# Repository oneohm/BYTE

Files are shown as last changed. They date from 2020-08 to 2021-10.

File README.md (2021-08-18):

# The BYTE
Full design package for the BYTE hands free interface

Details are available on the Hackaday project page:`
https://hackaday.io/project/171778-the-byte

## Repository Architecture

This repository is divided by 4 main folders:

- Docs: You'll find here our consult documents, and documentation of the project.
- Firmware: You'll find here everything you need to build the firmware and in case of needed, modify it.
- Hardware: You'll find here the KiCad projects with theirs libraries so the design is fully portable.
- Mechanical: You''ll find here all the FreeCad files to print/modify/understand the mechanics of the device.

You will find more information on each README in each folder, in order to keep this readme short.

# Previous Versions

It's important to note that this repository is under development, if your interested on one "The Byte" device already working, you should jump to the [Realese section](https://github.com/oneohm/BYTE/releases) of this repository to get the V1.0

## Version 1.0 

The version 1.0 has this architecture based on Seeeduino XIAO and all the connection is done by USB.

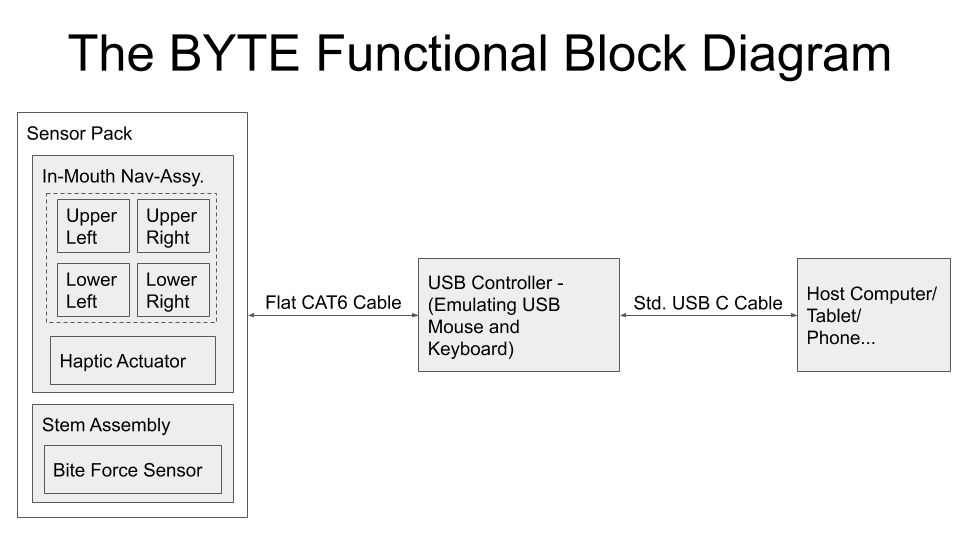
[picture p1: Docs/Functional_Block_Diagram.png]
Architecture


## License Info:

Firmware is licensed under the GNU General Public License v3.0

Hardware design is licensed under <br />This work is licensed under a <a rel="license" href="http://creativecommons.org/licenses/by-nc-sa/4.0/">Creative Commons Attribution-NonCommercial-ShareAlike 4.0 International License</a>.

Once the design is finalized the hardware will recieve a more permissive license.

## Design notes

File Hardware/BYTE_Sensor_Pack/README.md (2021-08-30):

# The BYTE
Full design package for the BYTE hands free interface

Details are available on the Hackaday project page:`
https://hackaday.io/project/171778-the-byte

# Sensor Pack 

 You'll find here the KiCad projects for the different sensor packs.

- BYTE_Sensors.pretty: Library folder for all the KiCad footprints used in the sensor pack development.

- BYTE_FSR: First sensor pack used, only FSR for X/Y axis.
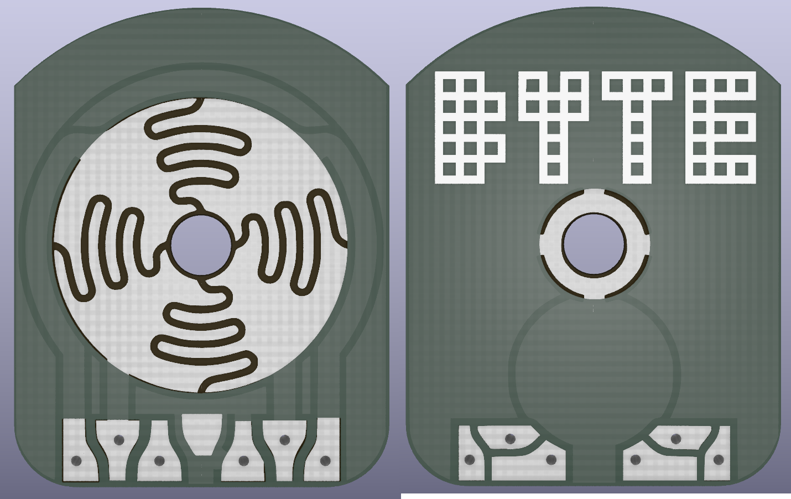
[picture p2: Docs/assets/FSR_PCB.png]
BYTE_FSR

- BYTE_Bite: First sensor pack used, only FSR also for the bite.
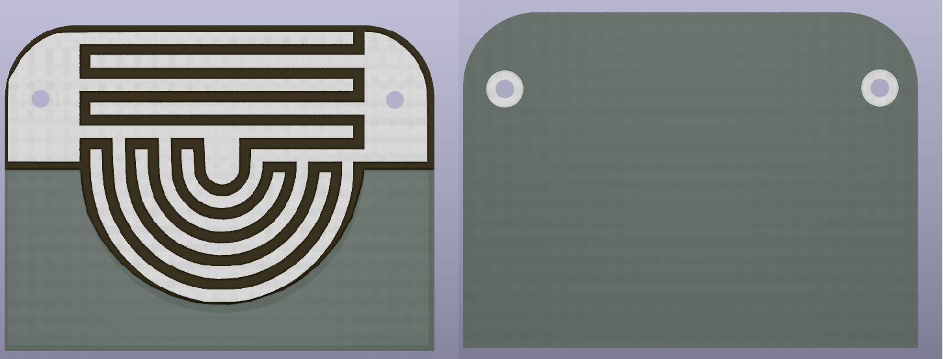
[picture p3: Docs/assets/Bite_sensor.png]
BYTE_Bite

- BYTE_Capacitive: Sensor intended to be used as capacitive feedback for FSR shift error.
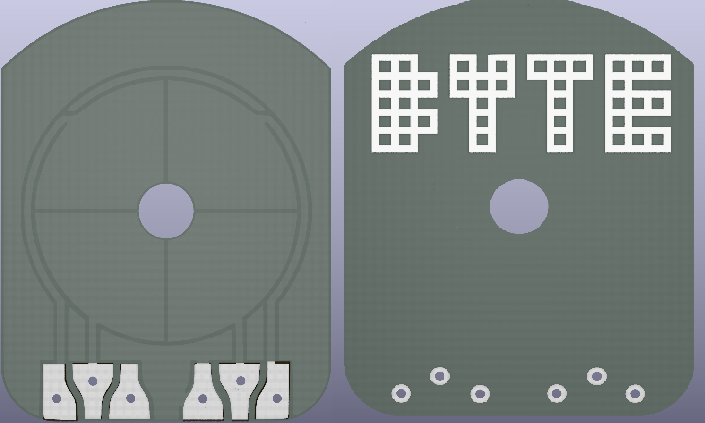
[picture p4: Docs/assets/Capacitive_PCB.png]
BYTE_Capacitive

- ...more to come.

## License Info:

Firmware is licensed under the GNU General Public License v3.0

Hardware design is licensed under <br />This work is licensed under a <a rel="license" href="http://creativecommons.org/licenses/by-nc-sa/4.0/">Creative Commons Attribution-NonCommercial-ShareAlike 4.0 International License</a>.

Once the design is finalized the hardware will recieve a more permissive license.

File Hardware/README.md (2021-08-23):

# The BYTE
Full design package for the BYTE hands free interface

Details are available on the Hackaday project page:`
https://hackaday.io/project/171778-the-byte

# Hardware 

 You'll find here the KiCad projects with theirs libraries so the design is fully portable among other folders with more hardware related information.

- BYTE_Bill_Of_Materials: Bill of materials of the electronics
- BYTE_Controller_PCB:  KiCad project for the main controller.
- BYTE_Full_Schematics: Full schematic in PDF for easy reading without KiCad.
- BYTE_Sensor_Artwork: All SVG files used to convert shapes from FreeCad to KiCad
- BYTE_Sensors_PCB: KiCad projects for the different sensor packs. 

You will find more information on each README in each folder, in order to keep this readme short.

## License Info:

Firmware is licensed under the GNU General Public License v3.0

Hardware design is licensed under <br />This work is licensed under a <a rel="license" href="http://creativecommons.org/licenses/by-nc-sa/4.0/">Creative Commons Attribution-NonCommercial-ShareAlike 4.0 International License</a>.

Once the design is finalized the hardware will recieve a more permissive license.

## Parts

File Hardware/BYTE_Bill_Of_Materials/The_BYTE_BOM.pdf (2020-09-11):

The BYTE BOM [For Prototypes - Production will differ]

Costs are approximate for custom parts

Quantity | Description | Part Type | Manufacturer Part# Unit | Qty per unit | Unit Cost | Extended Cost Product Page/Source/Design...
1 Stem Top - 3D printed, PETG, 100% infill | 3D Printed | N/A | EA | 1 | $0.50 | $0.50 https://github.com/oneohm/BYTE/blob/master/BYTE_Printed_Parts/BYTE_108_Stem_Top.amf
1 Stem Middle - 3D printed, PETG, 100% infill | 3D Printed | N/A | EA | 1 | $0.50 | $0.50 https://github.com/oneohm/BYTE/blob/master/BYTE_Printed_Parts/BYTE_108_Stem_Middle.amf
1 Stem Bottom - 3D printed, PETG, 100% infill | 3D Printed | N/A | EA | 1 | $0.50 | $0.50 https://github.com/oneohm/BYTE/blob/master/BYTE_Printed_Parts/BYTE_108_Stem_Bottom.amf
1 Wedge - 3D printed, PETG, 20% infill | 3D Printed | N/A | EA | 1 | $0.50 | $0.50 https://github.com/oneohm/BYTE/blob/master/BYTE_Printed_Parts/BYTE_108_Wedge.amf
1 Retainer - 3D printed, PETG, 100% infill | 3D Printed | N/A | EA | 1 | $0.50 | $0.50 https://github.com/oneohm/BYTE/blob/master/BYTE_Printed_Parts/BYTE_108_Retainer.amf
1 Nav-Button - 3D printed, PETG, 100% infill | 3D Printed | N/A | EA | 1 | $0.50 | $0.50 https://github.com/oneohm/BYTE/blob/master/BYTE_Printed_Parts/BYTE_108_Button.amf
1 Controller Enclosure Top - 3D printed, PETG, 100% infill | 3D Printed | N/A | EA | 1 | $0.50 | $0.50 https://github.com/oneohm/BYTE/blob/master/BYTE_Printed_Parts/Controller_Enclosure_06_Top.amf
1 Controller Enclosure Bottom - 3D printed, PETG, 100% infill | 3D Printed | N/A | EA | 1 | $0.50 | $0.50 https://github.com/oneohm/BYTE/blob/master/BYTE_Printed_Parts/Controller_Enclosure_06_Bottom.amf
1 Force Sensitive Disc - Laser Cut, VELOSTAT 1706 | Laser/Die Cut | 1706 | Pack | 144 | $13.65 | $0.09 https://www.ebay.com/itm/Velostat-Linqstat-Pressure-Sensitive-Conductive-Film-12-X-12-6-mil-thick/202262191322
1 Stem Force Sensitive Resistor - Laser Cut, VELOSTAT 1706 | Laser/Die Cut | 1706 | Pack | 576 | $13.65 | $0.02 https://www.ebay.com/itm/Velostat-Linqstat-Pressure-Sensitive-Conductive-Film-12-X-12-6-mil-thick/202262191322
1 Stem Resistor Adhesive - Cut from 3M 468MP | Laser/Die Cut | 12X12-6-468MP | Sheet | 576 | $5.53 | $0.01 https://www.digikey.com/product-detail/en/3m-tc/12X12-6-468MP/3M9720-ND
1 Common Contact - Laser cut, 0.1mm Copper sheet | Laser Cut/Etched | B07K9K1Z8C | Roll | 155 | $7.99 | $0.05 https://www.amazon.com/gp/product/B07K9K1Z8C
1 Silicone Disc - Punched from 0.032" sheet | Punched/Die Cut | RS-S50CFDA-4 | Sheet | 576 | $21.25 | $0.04 https://www.mscdirect.com/product/details/31939168
1 Nav Sensor PCB | Bare PCB | N/A | Panel | 3 | $3.00 | $1.00 https://github.com/oneohm/BYTE/tree/master/FreeCAD_BYTE_Model
1 Bite Sensor PCB | Bare PCB | N/A | Panel | 3 | $3.00 | $1.00 https://github.com/oneohm/BYTE/tree/master/FreeCAD_BYTE_Model
1 Controller PCB | Bare PCB | N/A | Panel | 3 | $3.00 | $1.00 https://github.com/oneohm/BYTE/tree/master/BYTE_Controller_PCB
1 8P8C (RJ45) Connector, Right Angle, Through Hole | PCB Component | 54602-908LF | EA | 1 | $0.62 | $0.62 https://www.digikey.com/product-detail/en/54602-908LF/609-1046-ND
6 Resistors - 1K, 0603 | PCB Component | RC0603JR-071KL | EA | 1 | $0.10 | $0.10 https://www.digikey.com/product-detail/en/yageo/RC0603JR-071KL/311-1-0KGRCT-ND/729624
1 Transistor - 2N7002, SOT23 | PCB Component | T2N7002BK,LM | EA | 1 | $0.16 | $0.16 https://www.digikey.com/product-detail/en/toshiba-semiconductor-and-storage/T2N7002BK-LM/T2N7002BKLMCT-ND
1 Diode - Schottky, SOD123 | PCB Component | BAT54GWJ | EA | 1 | $0.14 | $0.14 https://www.digikey.com/product-detail/en/nexperia-usa-inc/BAT54GWJ/1727-7328-1-ND
1 Microcontroller Module - Seeeduino XIAO | PCB Component | 102010328 | EA | 1 | $5.00 | $5.00 https://www.digikey.com/product-detail/en/seeed-technology-co-ltd/102010328/1597-102010328-ND/
1 Capacitor - Ceramic, 10uF, 0603 | PCB Component | 0603ZD106KAT2A | EA | 1 | $0.12 | $0.12 https://www.digikey.com/product-detail/en/avx-corporation/0603ZD106KAT2A/478-10766-1-ND
1 Solder in Standoff - M2x0.4, 2.5mm Height | PCB Component | 9774025243R | EA | 1 | $1.09 | $1.09 https://www.digikey.com/product-detail/en/w-rth-elektronik/9774025243R/732-7079-1-ND
1 Haptic Actuator - 8x3mm 12000RPM DC 3V, 80mA | PCB Component | A00000257 | Pack | 15 | $15.99 | $1.07 https://www.amazon.com/gp/product/B07HQTF4DJ
1 Enclosure - Food grade silicone | Enclosure | LB-Paci-S301 | Pack | 3 | $11.99 | $4.00 https://www.amazon.com/dp/B07TYK5G3W
1 Screw - M2x0.4, 6mm long, Button Head, Hex | Hardware | B07W5HBRMP | Box | 30 | $10.99 | $0.37 https://www.amazon.com/gp/product/B07W5HBRMP
1 Silicone O-Ring - 5x2x1.5mm | Hardware | a19111100ux0577 | Pack | 10 | $5.69 | $0.57 https://www.amazon.com/gp/product/B082ST728C
1 CAT 6 Flat Cable - 32AWG, 1/2 cable, stripped and tinned | Cable | B07P1S6VKP | Pack | 10 | $14.11 | $1.41 https://www.amazon.com/gp/product/B07P1S6VKP
$141.07 | $21.86

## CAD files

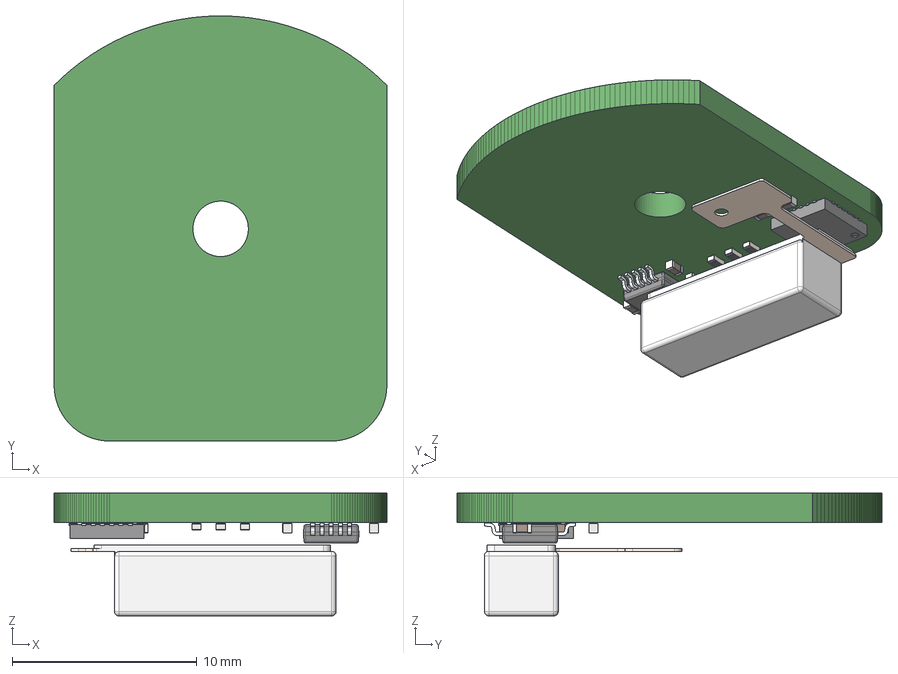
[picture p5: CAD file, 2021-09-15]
Hardware/BYTE_Sensor_Pack/BYTE_Capacitive/BYTE_Capacitive.step
18.0 x 23.0 x 6.65 mm

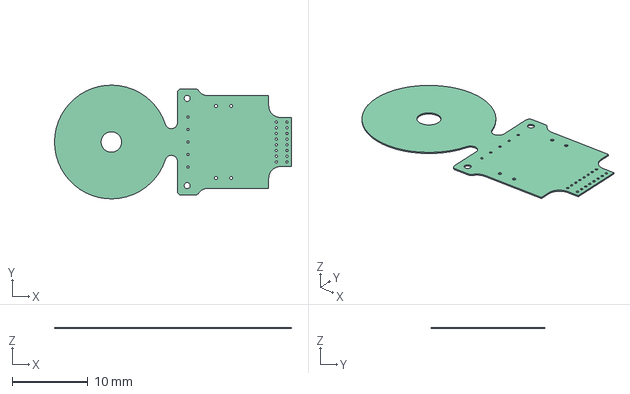
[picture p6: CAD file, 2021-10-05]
Hardware/BYTE_Sensor_Pack/BYTE_Flex/Flex_02/Flex_freecad_export.step
31.3 x 15.0 x 0.15 mm

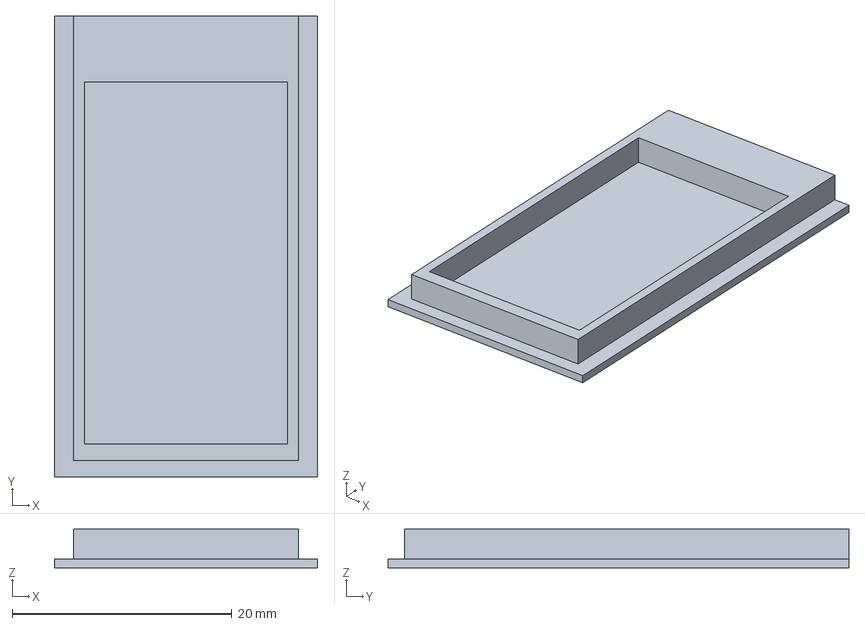
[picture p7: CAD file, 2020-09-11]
Mechanical/BYTE_Printed_Parts/Controller_Enclosure_06_Bottom.amf
24.0 x 42.0 x 3.55 mm

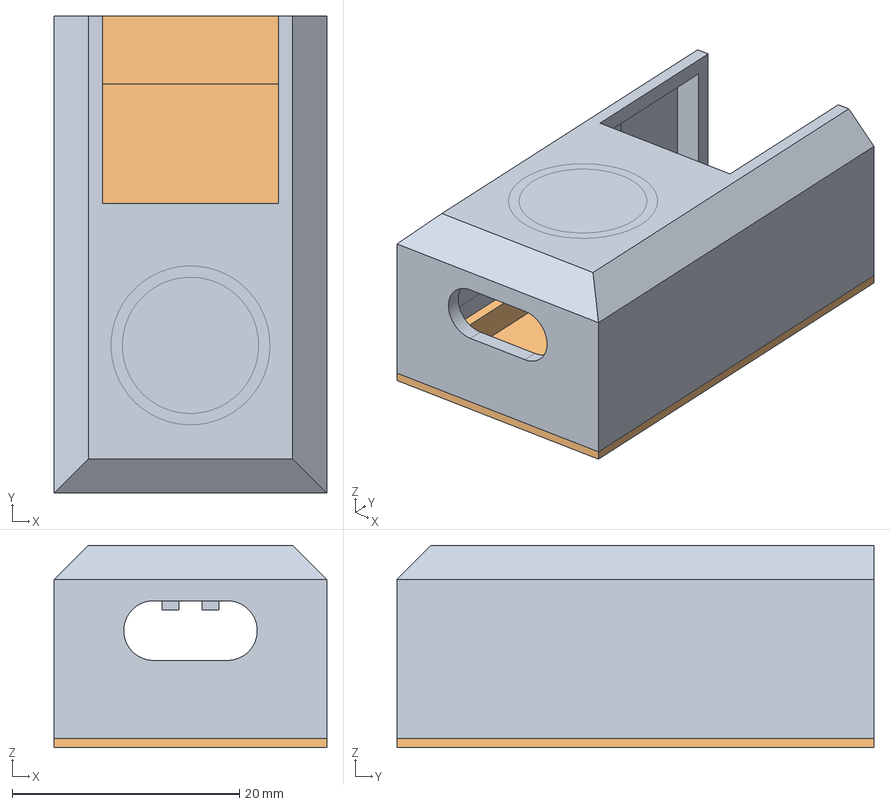
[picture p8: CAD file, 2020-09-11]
Mechanical/FreeCAD_BYTE_Model/Controller_Enclosure_06.FCStd
24.0 x 42.0 x 17.8 mm

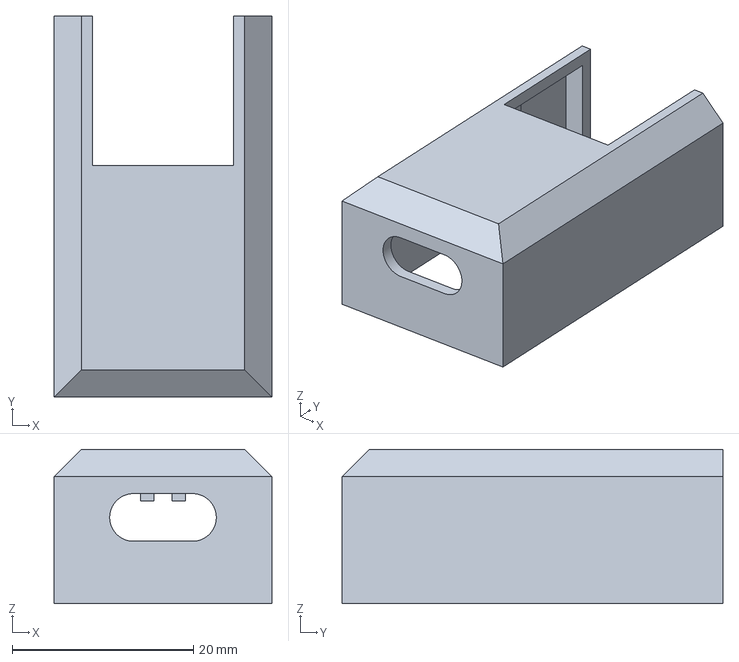
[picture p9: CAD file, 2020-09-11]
Mechanical/BYTE_Printed_Parts/Controller_Enclosure_06_Top.amf
24.0 x 42.0 x 17.0 mm

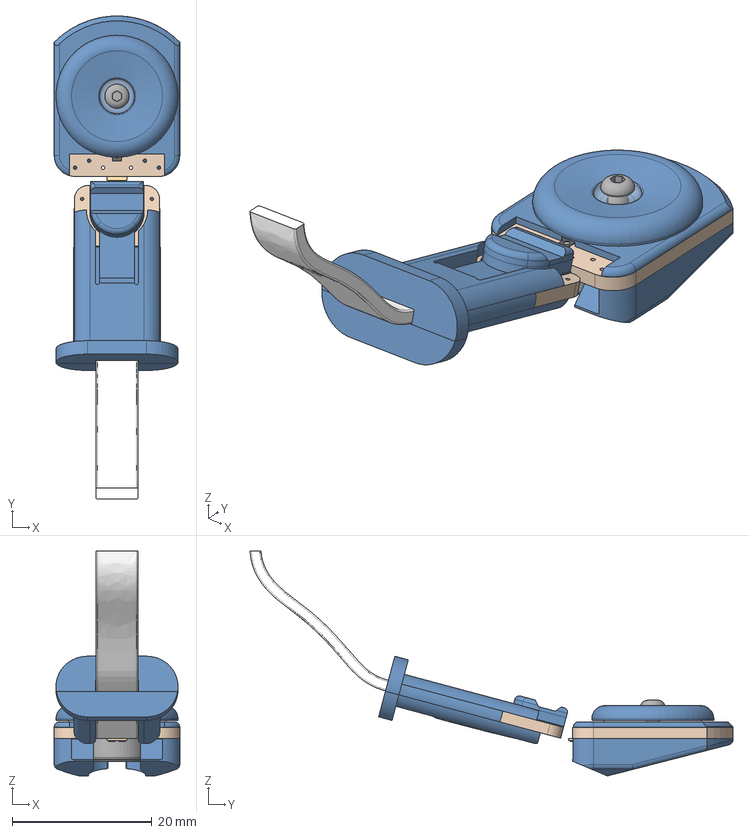
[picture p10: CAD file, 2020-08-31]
Mechanical/FreeCAD_BYTE_Model/Byte_108.FCStd
18.0 x 69.2 x 32.2 mm
PCB
Silicone_O-Ring
Motor_Body
Wire_Contacts
Foam_Pad
Motor_Contacts
Top
Middle
Bottom

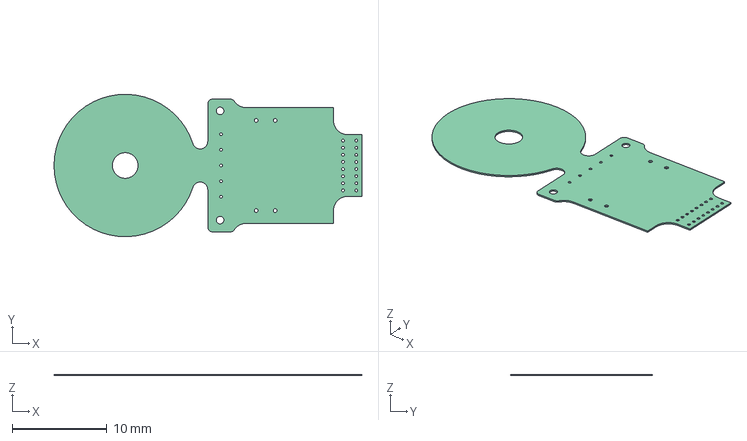
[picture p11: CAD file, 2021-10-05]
Hardware/BYTE_Sensor_Pack/BYTE_Flex/Flex_02/Flex_freecad_export_03.step
32.5 x 15.0 x 0.15 mm

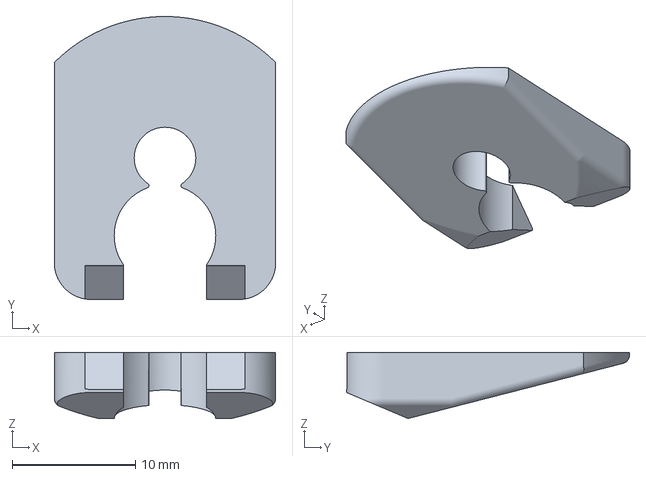
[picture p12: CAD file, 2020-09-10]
Mechanical/BYTE_Printed_Parts/BYTE_108_Wedge.amf
18.0 x 23.0 x 5.37 mm

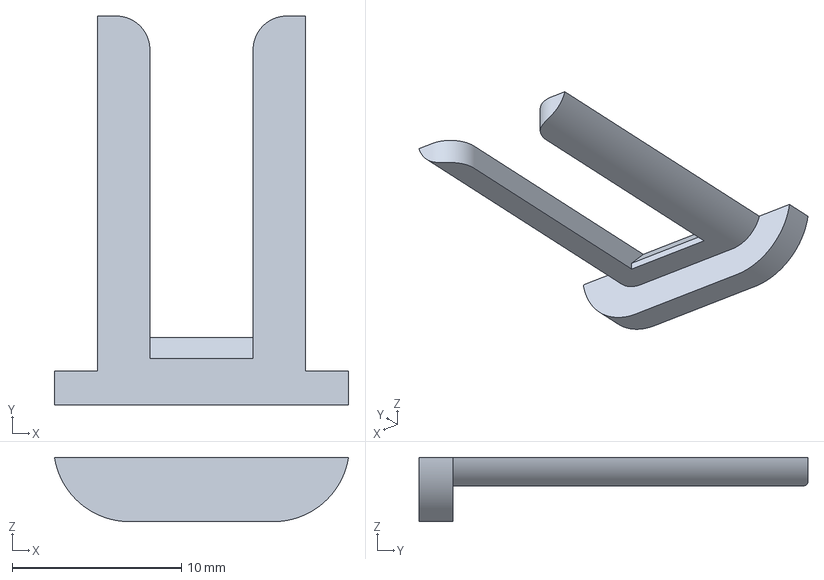
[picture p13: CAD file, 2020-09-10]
Mechanical/BYTE_Printed_Parts/BYTE_108_Stem_Bottom.amf
17.4 x 23.0 x 3.80 mm

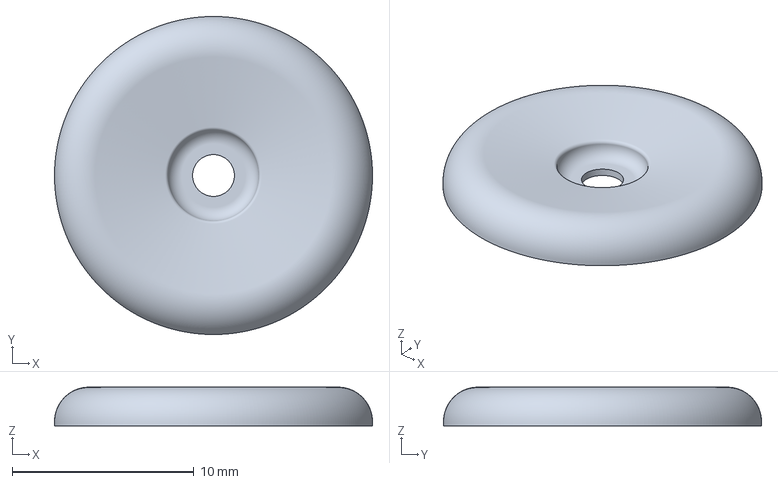
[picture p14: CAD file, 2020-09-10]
Mechanical/BYTE_Printed_Parts/BYTE_108_Button.amf
17.5 x 17.5 x 2.13 mm

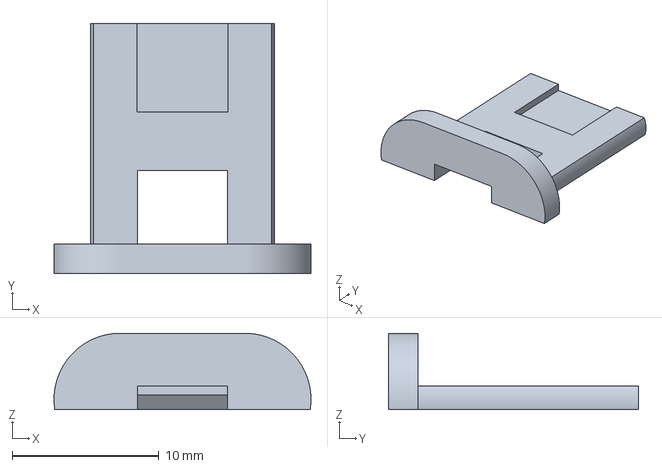
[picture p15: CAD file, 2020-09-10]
Mechanical/BYTE_Printed_Parts/BYTE_108_Stem_Middle.amf
17.5 x 17.0 x 5.20 mm

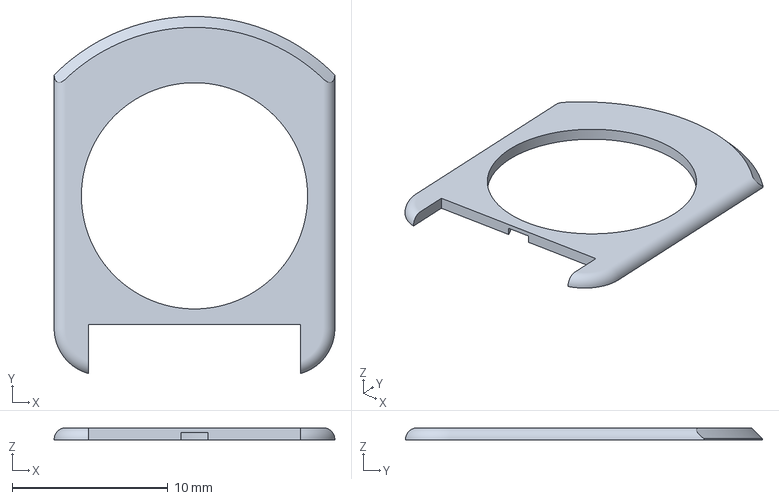
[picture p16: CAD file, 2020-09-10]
Mechanical/BYTE_Printed_Parts/BYTE_108_Retainer.amf
18.0 x 22.9 x 0.8 mm

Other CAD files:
Hardware/BYTE_Sensor_Pack/BYTE_Flex/Flex_02/Flex_Footprint_83.FCStd
Mechanical/BYTE_Printed_Parts/BYTE_108_Stem_Top.amf
Hardware/BYTE_Controller_PCB/BYTE_Controller_v2.2_Gerbers/BYTE_Control_Board-B_Mask.dxf
Hardware/BYTE_Controller_PCB/BYTE_Controller_v2.2_Gerbers/BYTE_Control_Board-F_Mask.dxf

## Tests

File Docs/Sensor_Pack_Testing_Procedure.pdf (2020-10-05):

# The BYTE Sensor Pack Testing Procedure

Instructions for manually testing the sensor pack and adjusting the preload force. [For production quantities an automated testing procedure will be developed]

The sensor pack should be adjusted for optimum performance and thoroughly tested before final assembly into the silicone enclosure and sealing against moisture ingress.

Required Equipment:
- Jumper Wires
- Bench Power Supply
- Multimeter
- RJ-45 Breakout board
Example part: https://www.amazon.com/gp/product/B0156JXSF8

Setup:
1. Set power supply to 3.3V
2. Configure multimeter for resistance measurement
3. Attach RJ-45 breakout board to the unit under test

Procedure:
1. Confirm the cable latch is functional and properly engaged
a. Visually inspect
b. Lightly pull and wiggle the cable to ensure a good connection
2. Test the haptic actuator
a. Measure the resistance between pins 7 and 8
i. The resistance should be approximately 50 ohms
b. Using jumper wires briefly connect the power supply (3.3V) to pins 7 and 8
i. Confirm the haptic actuator vibrates, and remains securely adhered.
3. Test the bite force sensor
a. Measure the resistance between pins 1 and 2
i. The resistance should be >= 10k ohms
b. Squeeze the bite force sensor between the thumb and forefinger while monitoring the resistance.
i. Confirm the resistance varies smoothly in response to squeeze pressure ii. The resistance should be approximately 500 ohms when squeezed firmly
4. Initial nav-button sensor test
a. Lightly tighten the preload screw (finger tight)

b. Test upper right quadrant
i. Measure unloaded resistance between pins 6 and 7
ii. | Confirm the resistance is between 30k and 100k ohms
iii. | Press the upper left of the nav-button while monitoring the resistance
iv. | Confirm the resistance decreases smoothly with the applied pressure
v. The resistance should be approximately 500 ohms while squeezed firmly
c. Test upper left quadrant
i. Measure unloaded resistance between pins 5 and 7
ii. | Confirm the resistance is between 30k and 100k ohms
iii. | Press the upper left of the nav-button while monitoring the resistance
iv. | Confirm the resistance decreases smoothly with the applied pressure
v. The resistance should be approximately 500 ohms while squeezed firmly
d. Test lower right quadrant
i. Measure unloaded resistance between pins 4 and 7
ii. | Confirm the resistance is between 30k and 100k ohms
iii. | Press the upper left of the nav-button while monitoring the resistance
iv. | Confirm the resistance decreases smoothly with the applied pressure
v. The resistance should be approximately 500 ohms while squeezed firmly
e. Test lower left quadrant
i. Measure unloaded resistance between pins 3 and 7
ii. | Confirm the resistance is between 30k and 100k ohms
iii. | Press the upper left of the nav-button while monitoring the resistance
iv. | Confirm the resistance decreases smoothly with the applied pressure
v. The resistance should be approximately 500 ohms while squeezed firmly
f. Confirm that all four sensor zones respond similarly and there are no outliers
5. Adjust nav-sensor preload force
a. Remove the preload screw and apply a small drop of red threadlock near the tip
b. Re-install the preload screw and lightly tighten (finger tight)
c. Attach the multimeter to pins 3 and 6
d. While monitoring the resistance adjust the screw until the multimeter shows approximately 60k ohms.

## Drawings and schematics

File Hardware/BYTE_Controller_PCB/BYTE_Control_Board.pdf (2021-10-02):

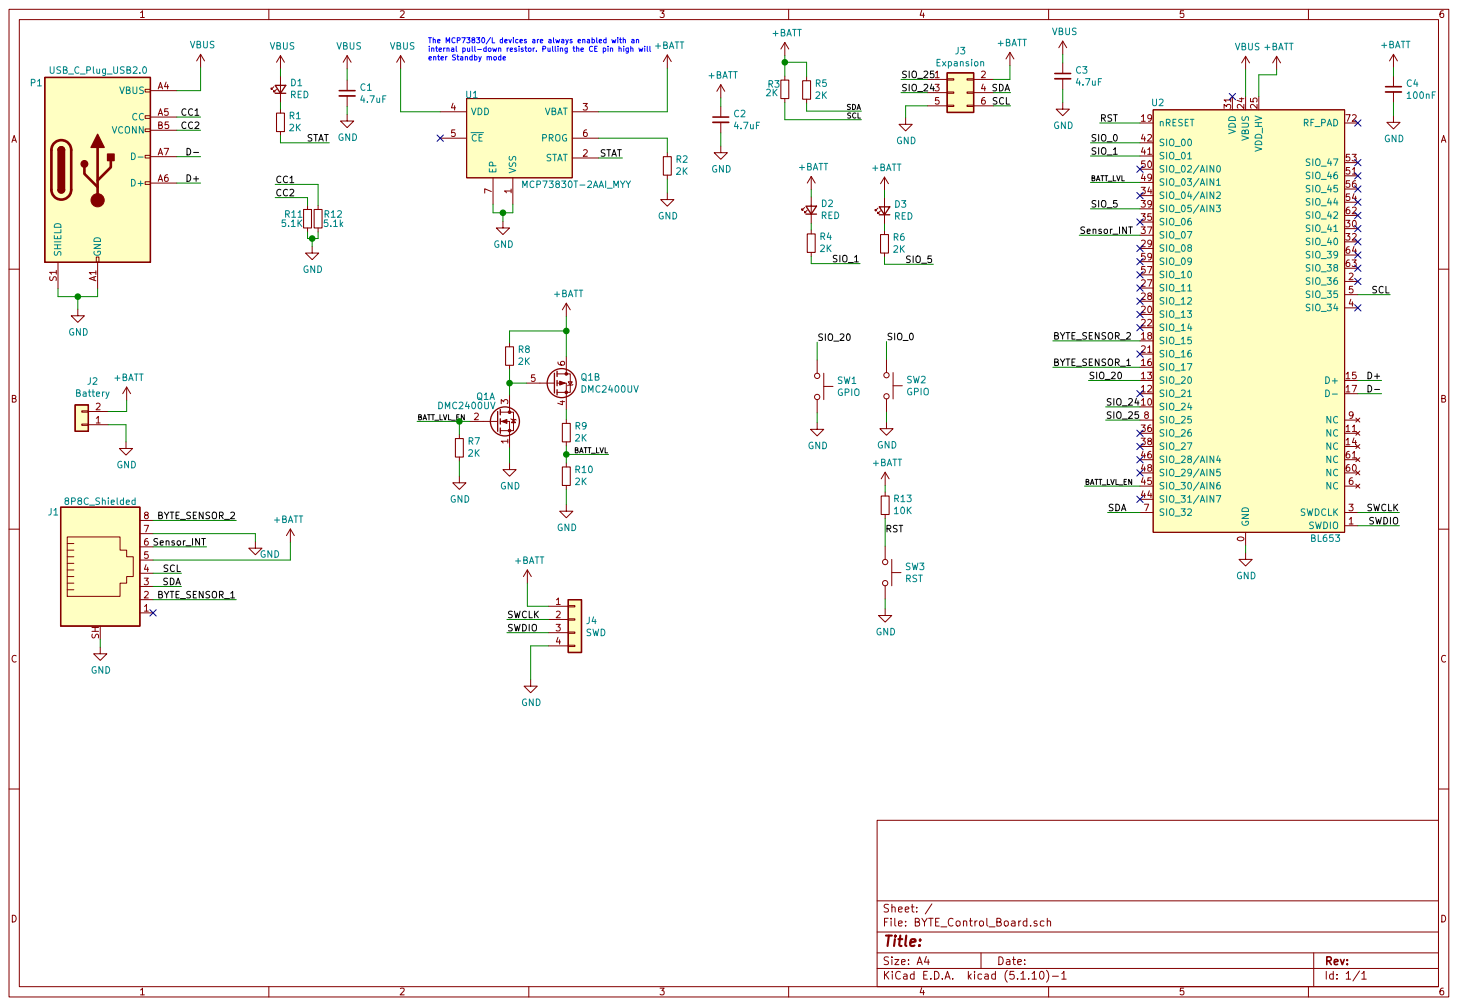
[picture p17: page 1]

The MCP73830/L devices are always enabled with an
internal pull-down resistor. Pulling the CE pin high will enter Standby mode

1 STAT 2 VBAT 3 VDD 4 CE 5 PROG 6 EP

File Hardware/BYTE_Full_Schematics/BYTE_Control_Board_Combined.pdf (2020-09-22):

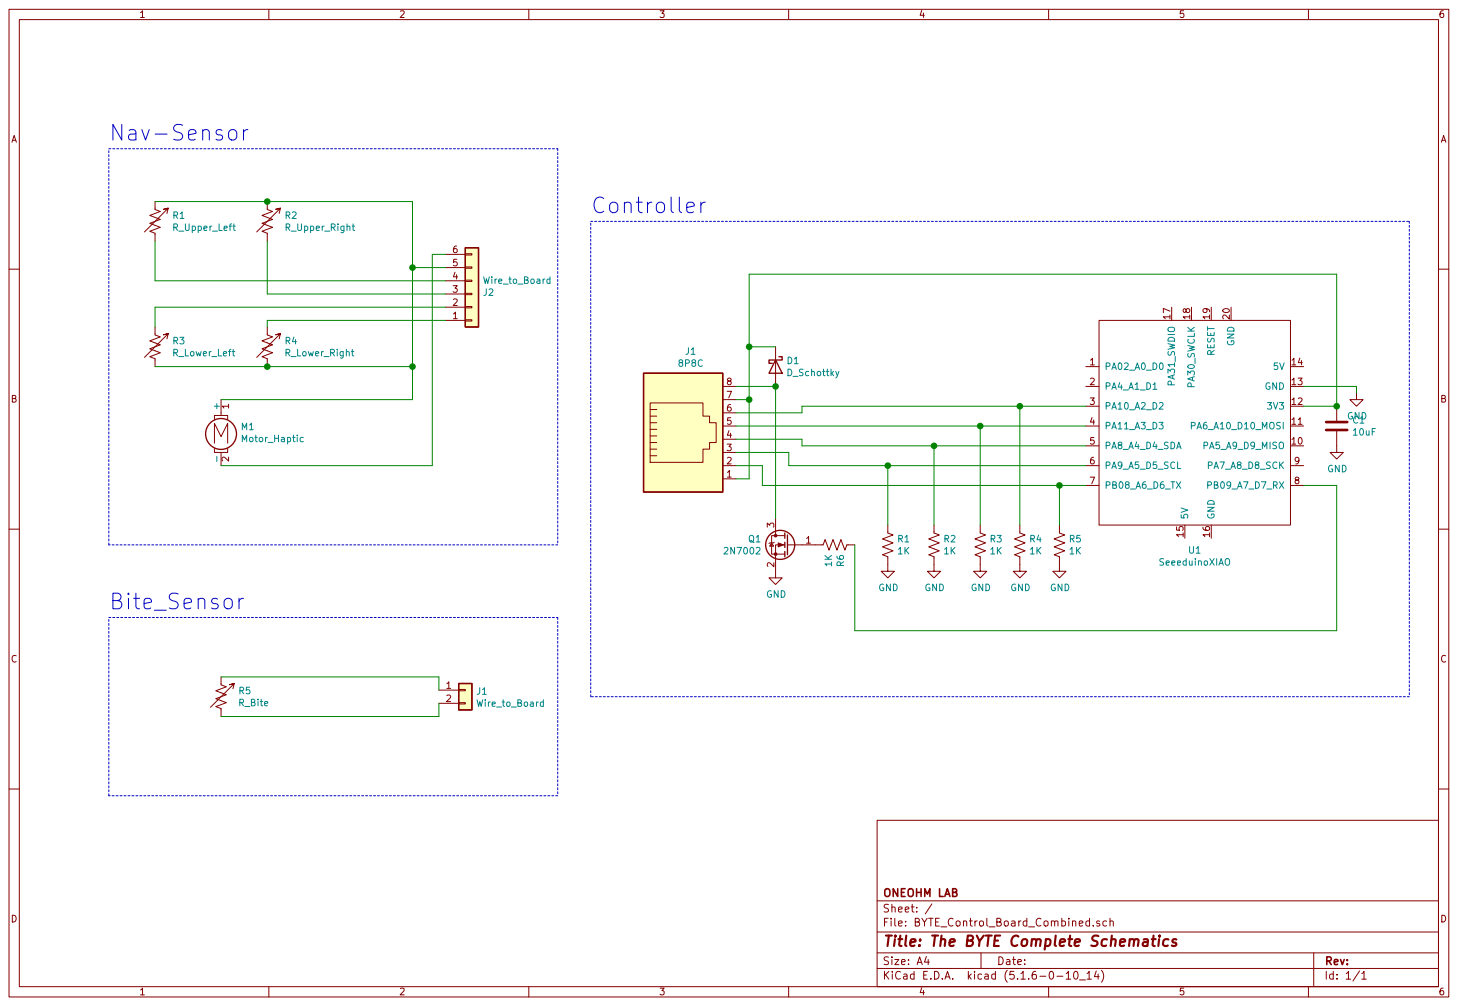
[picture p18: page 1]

-2 M1Motor_Haptic R5 R_Bite GND GND GND GND GND GND

File: BYTE_Control_Board_Combined.sch Sheet: / ONEOHM LAB

Id: 1/1 Title: The BYTE Complete Schematics

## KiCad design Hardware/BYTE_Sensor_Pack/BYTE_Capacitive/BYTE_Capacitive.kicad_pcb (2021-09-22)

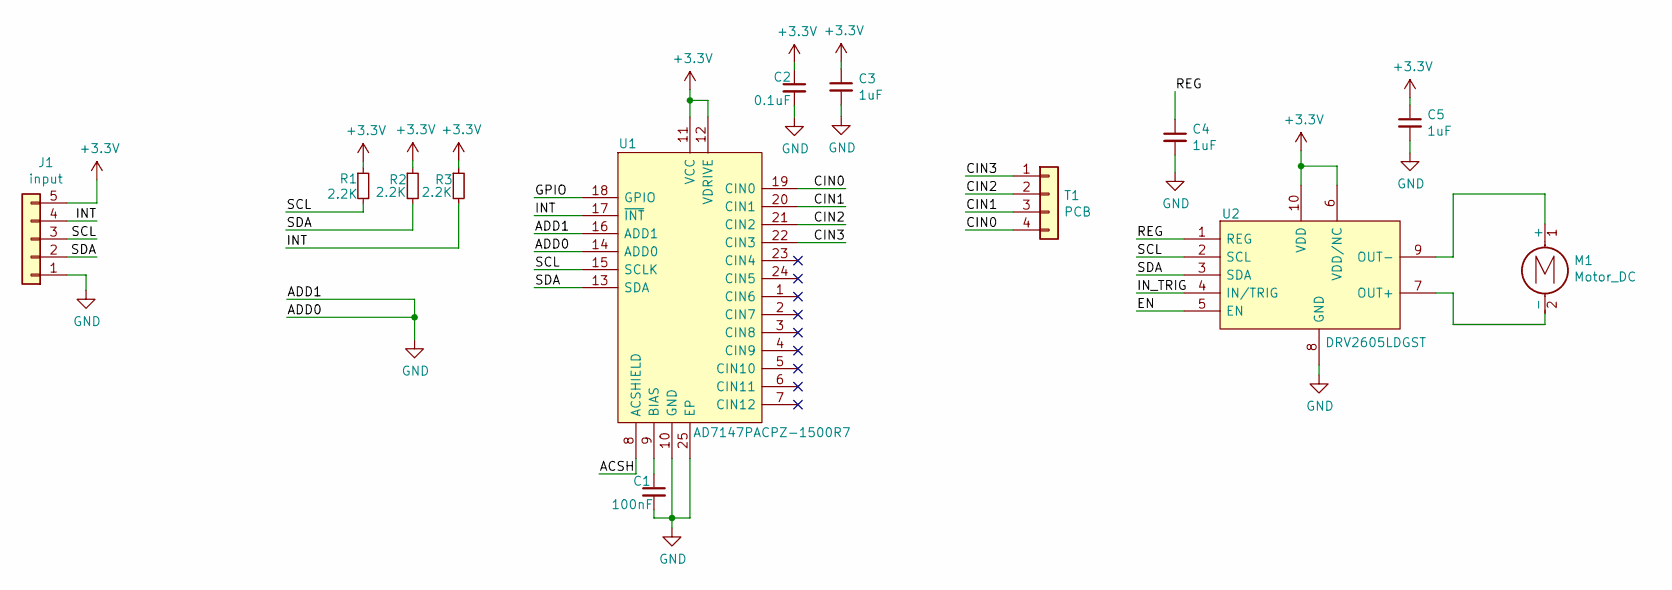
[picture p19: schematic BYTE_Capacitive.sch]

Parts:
C1: 100nF; C_0402_1005Metric
C2: 0.1uF; C_0402_1005Metric
C3, C4, C5: 1uF; C_0402_1005Metric
J1: input; Flex_Connector
M1: Motor_DC; VLV041235L
R1, R2, R3: 2.2K; R_0402_1005Metric
T1: PCB; Capacitive_PCB_NoConnector
U1: AD7147PACPZ-1500R7; QFN50P400X400X80-25N-D
U2: DRV2605LDGST; SOP50P490X110-10N

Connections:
+3V3: C2.1, C3.1, C5.1, J1.5, R1.1, R2.1, R3.1, U1.11 (VCC), U1.12 (VDRIVE), U2.6 (VDD/NC), U2.10 (VDD)
/ACSH: U1.8 (ACSHIELD)
/CIN0: T1.4, U1.19 (CIN0)
/CIN1: T1.3, U1.20 (CIN1)
/CIN2: T1.2, U1.21 (CIN2)
/CIN3: T1.1, U1.22 (CIN3)
/EN: U2.5 (EN)
/GPIO: U1.18 (GPIO)
/INT: J1.4, R3.2, U1.17 (~INT)
/IN_TRIG: U2.4 (IN/TRIG)
/REG: C4.1, U2.1 (REG)
/SCL: J1.3, R1.2, U1.15 (SCLK), U2.2 (SCL)
/SDA: J1.2, R2.2, U1.13 (SDA), U2.3 (SDA)
GND: C1.2, C2.2, C3.2, C4.2, C5.2, J1.1, U1.10 (GND), U1.14 (ADD0), U1.16 (ADD1), U1.25 (EP), U2.8 (GND)
unnamed: C1.1, U1.9 (BIAS)
unnamed: M1.1 (+), U2.9 (OUT-)
unnamed: M1.2 (-), U2.7 (OUT+)

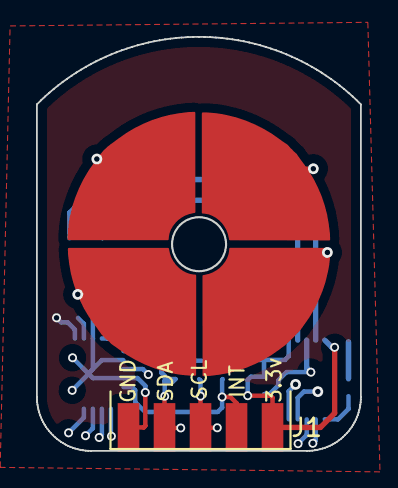
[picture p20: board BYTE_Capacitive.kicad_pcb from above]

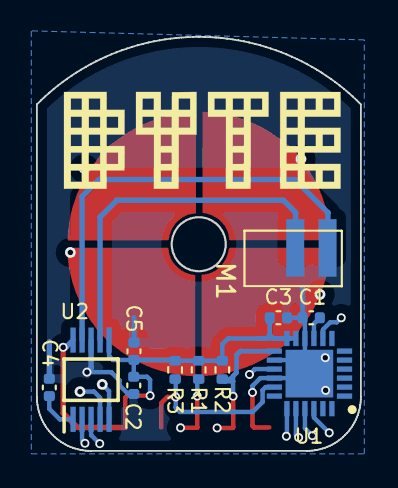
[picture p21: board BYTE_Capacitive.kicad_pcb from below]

Board: 4 copper layers, 18.0 x 23.0 mm, 14 parts (11 on the bottom side), 13 nets.

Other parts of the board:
Ref**: Val**; Logo

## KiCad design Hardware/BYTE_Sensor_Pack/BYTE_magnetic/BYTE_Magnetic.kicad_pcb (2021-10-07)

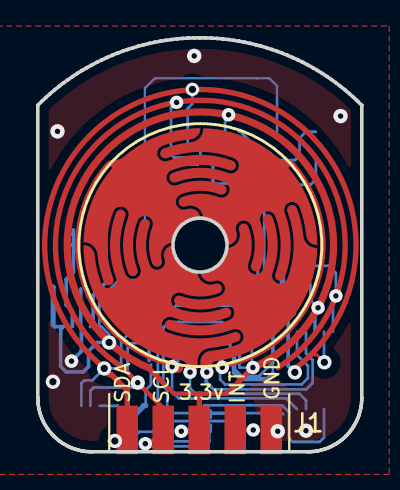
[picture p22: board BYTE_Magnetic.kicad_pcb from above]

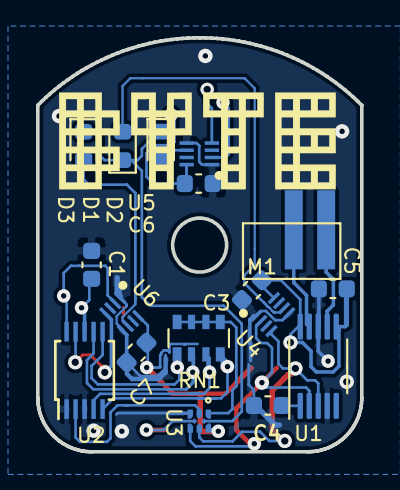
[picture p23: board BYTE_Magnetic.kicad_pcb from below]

Board: 2 copper layers, 18.0 x 23.0 mm, 19 parts (17 on the bottom side), 18 nets.

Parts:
C1, C4, C5: 1uF; C_0603_1608Metric
C3, C6, C7: 0.1uF; C_0603_1608Metric
D1, D2, D3: D_Small; D_0603_1608Metric
J1: Input; Flex_Connector
M1: Motor_DC; VLV041235L
RN1: R_Pack04; R_Array_Convex_4x0603
Ref**: Val**; Logo
U1: DRV2605LDGS; VSSOP-10_3x3mm_P0.5mm
U2: ADS1115IDGS; TSSOP-10_3x3mm_P0.5mm
U3: PTCA9536BDTMR; PTCA9416DTMR
U4: SI7210-B-12-IM2; SON40P140X160X40-8N-D
U5: SI7210-B-13-IM2; SON40P140X160X40-8N-D
U6: SI7210-B-14-IM2; SON40P140X160X40-8N-D

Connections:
+3V3: C1.1, C3.1, C5.1, C6.1, C7.1, J1.3, U1.6, U1.10, U2.8, U3.7, U4.8, U5.8, U6.8
/A0: RN1.3, U2.4
/A1: RN1.4, U2.5
/A2: RN1.1, U2.6
/A3: RN1.2, U2.7
/ALERT: U2.2, U3.2
/FSR_CTRL: RN1.5, RN1.6, RN1.7, RN1.8, U3.1
/INT_OUT: J1.4, U3.4
/SCL: J1.2, U1.2, U2.10, U3.5, U4.2, U5.2, U6.2
/SDA: J1.1, U1.3, U2.9, U3.6, U4.4, U5.4, U6.4
/magneticSignal: D1.1, D2.1, D3.1, U3.8
GND: C1.2, C3.2, C4.2, C5.2, C6.2, C7.2, J1.5, U1.4, U1.8, U2.1, U2.3, U3.3, U4.1, U4.5, U5.1, U5.5, U6.1, U6.5
unnamed: C4.1, U1.1
unnamed: D1.2, U4.6
unnamed: D2.2, U5.6
unnamed: D3.2, U6.6
unnamed: M1.1, U1.7
unnamed: M1.2, U1.9

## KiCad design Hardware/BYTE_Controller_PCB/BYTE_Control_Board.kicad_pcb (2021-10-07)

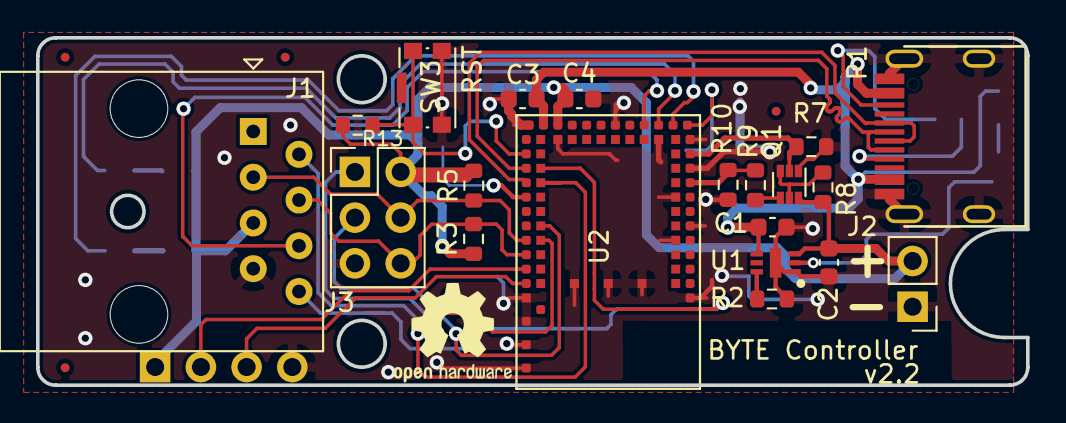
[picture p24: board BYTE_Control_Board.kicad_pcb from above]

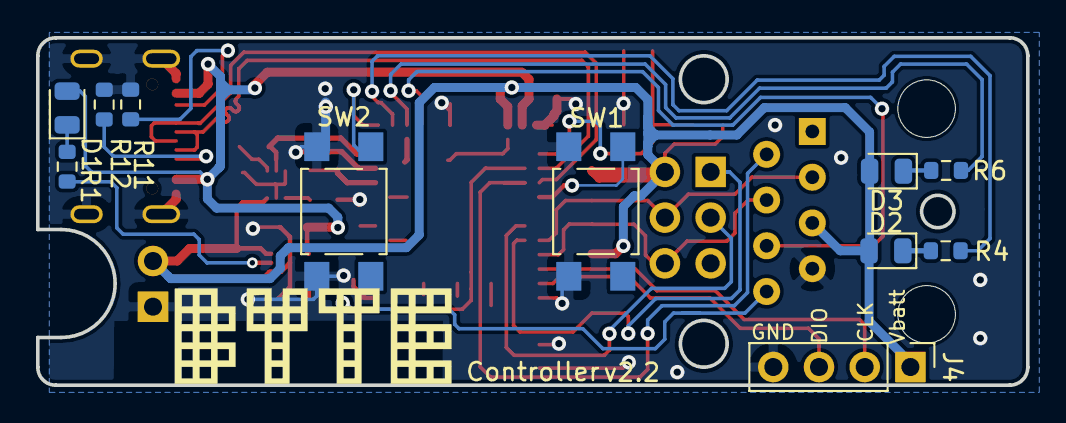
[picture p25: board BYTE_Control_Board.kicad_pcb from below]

Board: 2 copper layers, 55.0 x 19.3 mm, 32 parts (11 on the bottom side), 30 nets.

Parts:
C1, C2, C3: 4.7uF; C_0603_1608Metric
C4: 100nF; C_0603_1608Metric
D1, D2, D3: RED; LED_0805_2012Metric
J1: 8P8C_Shielded; RJ45_Amphenol_54602-x08_Horizontal
J2: Battery; PinHeader_1x02_P2.54mm_Vertical
J3: Expansion; PinHeader_2x03_P2.54mm_Vertical
J4: SWD; PinHeader_1x04_P2.54mm_Vertical
P1: USB_C_Plug_USB2.0; C393939
Q1: DMC2400UV; SOT-563
R1, R2, R3, R4, R5, R6, R7, R8, R9, R10: 2K; R_0603_1608Metric
R11: 5.1K; R_0603_1608Metric
R12: 5.1k; R_0603_1608Metric
R13: 10K; R_0603_1608Metric
Ref**: Val**; Logo
SW1, SW2: GPIO; SW_SPST_TL3305A
SW3: RST; SW_Push_1P1T-SH_NO_CK_KMR2xxG
U1: MCP73830T-2AAI_MYY; 2x2TDFN
U2: BL653; BL653_v5

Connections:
+BATT: C2.1, C4.1, D2.2, D3.2, J1.5, J2.2, J3.2, J4.1, Q1.6, R3.2, R5.2, R8.2, R13.2, U1.3, U2.25
/BATT_LVL: R9.1, R10.2, U2.49
/BATT_LVL_EN: Q1.2, R7.2, U2.45
/BYTE_SENSOR_1: J1.2, U2.16
/BYTE_SENSOR_2: J1.8, U2.18
/CC1: P1.A5, R12.1
/CC2: P1.B5, R11.2
/D+: P1.A6, U2.15
/D-: P1.A7, U2.17
/RST: R13.1, SW3.1, U2.19
/SCL: J1.4, J3.6, R3.1, U2.5
/SDA: J1.3, J3.4, R5.1, U2.7
/SIO_0: SW2.1, U2.42
/SIO_1: R4.1, U2.41
/SIO_5: R6.1, U2.39
/SIO_20: SW1.1, U2.13
/SIO_24: J3.3, U2.10
/SIO_25: J3.1, U2.8
/STAT: R1.1, U1.2
/SWCLK: J4.2, U2.3
/SWDIO: J4.3, U2.1
/Sensor_INT: J1.6, U2.37
GND: C1.2, C2.2, C3.2, C4.2, J1.7, J2.1, J3.5, J4.4, P1.A1, P1.S1, Q1.1, R2.1, R7.1, R10.1, R11.1, R12.2, SW1.2, SW2.2, SW3.2, U1.1, U1.7, U2.0, U2.23, U2.26, U2.33, U2.40, U2.43, U2.47, U2.52, U2.55, U2.58, U2.65, U2.66, U2.67, U2.68, U2.69, U2.70, U2.71
unnamed: D1.1, R1.2
unnamed: D2.1, R4.2
unnamed: D3.1, R6.2
unnamed: Q1.3, Q1.5, R8.1
unnamed: Q1.4, R9.2
unnamed: R2.2, U1.6
VBUS: C1.1, C3.1, D1.2, P1.A4, U1.4, U2.24

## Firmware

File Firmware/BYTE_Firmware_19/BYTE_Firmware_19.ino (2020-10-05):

/*  The BYTE interface firmware
    Copyright (C) 2020  oneohm

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
    http://github.com/oneohm/BYTE
*/

#include <Mouse.h>
#include <Keyboard.h>
#include <FlashStorage.h>

// Create a structure to contain all of the calibration data
// The "valid" variable is set to "true" after
// the structure is filled with actual data for the first time.
typedef struct {
  bool valid;
  int biteBaselineOffset;
  int liteBiteThreshold;
  int firmBiteThreshold;
  int baselineOffset[4];
  int fsrMax[4]; 
} CalibrationData;

// Reserve a portion of flash memory for the calibration data
FlashStorage(calibration_storage, CalibrationData);

// Create a variable for handling the calibration
CalibrationData cal;

// Pin Mapping
const unsigned int bitePin = 6;
const unsigned int hapticPin = 7;
//const unsigned int fsrPins[4] = {2,3,4,5}; 
const unsigned int fsrPins[4] = {3,2,4,5}; //Upper right and left pins swapped in actual prototype...

// Predefined calibration values
//const int moveTreshold = 1;
const int maxMovement = 10;
const int scrollThreshold = 6;
const int pushClickForce = 30;
const float forceScalerX = 0.1; // 0.3 works OK
const float forceScalerY = 0.1; // 0.12 works OK
const float inertiaFactor = 0.15; // 0.5 might be a bit too much

bool isBit = false;
bool longClicked = false;
bool pressClicked = false;
int fsrReadings[4] = {0,0,0,0};
int biteReading = 0;
int previousMoveX = 0;
int previousMoveY = 0;
float xAccumulator = 0;
float yAccumulator = 0;
int lastMoveMagnitude = 0;
int lastForceMagnitude = 0;

// Timing configuration
unsigned long restTimer = 0;
unsigned long previousMillis = 0; // Stores the last time the loop was run
unsigned long clickStartTime = 0; // Keeps track of click length
const unsigned int captureWindow = 3000; //Number of milliseconds to monitor the pin during calibration
const unsigned long updateInterval = 8; // Standard mice have a 125Hz polling rate (~8ms between samples)
const unsigned long longClickTime = 2000; // milliseconds required to trigger a long click
const unsigned long driftRestPeriod = 550; // milliseconds of rest to trigger drift compensation

// Drift compensation
int driftDetectionForce = 0;
const int driftDetectionChange = 2;

void getOffsets(void){
  //TODO Better to collect several samples, rather than just one...
  for(int index = 0; index <= 3; index++){
    cal.baselineOffset[index]=analogRead(fsrPins[index]);
  }
  cal.biteBaselineOffset = analogRead(bitePin);
}

// Useful to periodically reset the "at rest" offests to deal with sensor drift
void resetOffsets(void){
  for(int index = 0; index <= 3; index++){
    cal.baselineOffset[index]=analogRead(fsrPins[index]);
  }
}

// Open a new text document and guide the user through calibration
// This is for OSX, needs to be changed for other platforms...
void calibrate(void){
  Keyboard.press(KEY_LEFT_GUI);
  delay(100);
  Keyboard.press(' ');
  delay(500);
  Keyboard.releaseAll();
  delay(500);
  Keyboard.print("textEdit");
  delay(100);
  Keyboard.press(KEY_RETURN);
  delay(100);
  Keyboard.releaseAll();
  delay(500);
  Keyboard.press(KEY_LEFT_GUI);
  delay(100);
  Keyboard.press('n');
  delay(500);
  Keyboard.releaseAll();
  delay(1500);
  Keyboard.println("BYTE Calibration");
  Keyboard.press(KEY_RETURN);
  delay(100);
  Keyboard.releaseAll();
  delay(100);
  Keyboard.press(KEY_RETURN);
  delay(100);
  Keyboard.releaseAll();
  Keyboard.println("Setting the baseline.");
  Keyboard.press(KEY_RETURN);
  delay(100);
  Keyboard.releaseAll(); 
  Keyboard.println("Hold the BYTE comfortably at rest...");
  Keyboard.press(KEY_RETURN);
  delay(1000);
  Keyboard.releaseAll(); 
  getOffsets();
  Keyboard.print("  Baseline established");
  Keyboard.press(KEY_RETURN);
  delay(100);
  Keyboard.releaseAll();
  Keyboard.press(KEY_RETURN);
  delay(100);
  Keyboard.releaseAll();  
  Keyboard.println("First set the motion activation force (lite bite).");
  Keyboard.press(KEY_RETURN);
  delay(100);
  Keyboard.releaseAll(); 
  Keyboard.println("Apply the desired pressure...");
  Keyboard.press(KEY_RETURN);
  delay(100);
  Keyboard.releaseAll(); 
  cal.liteBiteThreshold = capturePressure(bitePin);
  Keyboard.print("  Set to: ");
  Keyboard.println(cal.liteBiteThreshold);
  Keyboard.press(KEY_RETURN);
  delay(100);
  Keyboard.releaseAll();
  Keyboard.press(KEY_RETURN);
  delay(100);
  Keyboard.releaseAll();  
  Keyboard.println("Now set the click force (firm bite).");
  Keyboard.press(KEY_RETURN);
  delay(100);
  Keyboard.releaseAll(); 
  Keyboard.println("Apply the desired pressure...");
  Keyboard.press(KEY_RETURN);
  delay(100);
  Keyboard.releaseAll(); 
  cal.firmBiteThreshold = capturePressure(bitePin);
  Keyboard.print("  Set to: ");
  Keyboard.println(cal.firmBiteThreshold);
  Keyboard.press(KEY_RETURN);
  delay(100);
  Keyboard.releaseAll();
  Keyboard.press(KEY_RETURN);
  delay(100);
  Keyboard.releaseAll(); 
  Keyboard.println("Now set the mouse upper left movement pressure.");
  Keyboard.press(KEY_RETURN);
  delay(100);
  Keyboard.releaseAll(); 
  Keyboard.println("Apply the maximum desired pressure...");
  Keyboard.press(KEY_RETURN);
  delay(100);
  Keyboard.releaseAll();
  cal.fsrMax[0] = capturePressure(fsrPins[0]);
  Keyboard.print("  Set to: ");
  Keyboard.println(cal.fsrMax[0]);
  Keyboard.press(KEY_RETURN);
  delay(100);
  Keyboard.releaseAll(); 
  Keyboard.press(KEY_RETURN);
  delay(100);
  Keyboard.releaseAll(); 
  Keyboard.println("Now set the mouse upper right movement pressure");
  Keyboard.press(KEY_RETURN);
  delay(100);
  Keyboard.releaseAll(); 
  Keyboard.println("Apply the maximum desired pressure...");
  Keyboard.press(KEY_RETURN);
  delay(100);
  Keyboard.releaseAll();
  cal.fsrMax[1] = capturePressure(fsrPins[1]);
  Keyboard.print("  Set to: ");
  Keyboard.println(cal.fsrMax[1]);
  Keyboard.press(KEY_RETURN);
  delay(100);
  Keyboard.releaseAll();
  Keyboard.press(KEY_RETURN);
  delay(100);
  Keyboard.releaseAll(); 
  Keyboard.println("Now set the mouse lower left movement pressure.");
  Keyboard.press(KEY_RETURN);
  delay(100);
  Keyboard.releaseAll(); 
  Keyboard.println("Apply the maximum desired pressure...");
  Keyboard.press(KEY_RETURN);
  delay(100);
  Keyboard.releaseAll(); 
  cal.fsrMax[2] = capturePressure(fsrPins[2]);
  Keyboard.print("  Set to: ");
  Keyboard.println(cal.fsrMax[2]);
  Keyboard.press(KEY_RETURN);
  delay(100);
  Keyboard.releaseAll();
  Keyboard.press(KEY_RETURN);
  delay(100);
  Keyboard.releaseAll(); 
  Keyboard.println("Now set the mouse lower right movement pressure.");
  Keyboard.press(KEY_RETURN);
  delay(100);
  Keyboard.releaseAll(); 
  Keyboard.println("Apply the maximum desired pressure...");
  Keyboard.press(KEY_RETURN);
  delay(100);
  Keyboard.releaseAll(); 
  cal.fsrMax[3] = capturePressure(fsrPins[3]);
  Keyboard.print("  Set to: ");
  Keyboard.println(cal.fsrMax[3]);
  Keyboard.press(KEY_RETURN);
  delay(100);
  Keyboard.releaseAll();
  Keyboard.press(KEY_RETURN);
  delay(100);
  Keyboard.releaseAll();    
}

// Calibration sanity check
bool check_calibration(void){
  bool isCalibrationGood = true;
  
  // Make sure the navigation baseline values are larger than the max values  
  for(int index = 0; index <= 3; index++){
    if(cal.baselineOffset[index] >= cal.fsrMax[index]){
      // the baseline and max sensor values are too close - bad calibration
      isCalibrationGood = false;
    } 
  }
  // Make sure the bite baseline values are larger than the max values  
  if(cal.biteBaselineOffset >= cal.liteBiteThreshold){
      // the baseline and max sensor values are too close - bad calibration
      isCalibrationGood = false;    
  }
  // Make sure firm bite threshold is higher than lite bite pressure threshold
  if(cal.liteBiteThreshold >= cal.firmBiteThreshold){
      // the baseline and max sensor values are too close - bad calibration
      isCalibrationGood = false;       
  }  
  return isCalibrationGood;
}

// Measure the adc pin and find the max value asserted in the next two seconds
int capturePressure(unsigned int adcPin){
  unsigned long time_now = 0; 
  int currentValue = 0;
  int maxValue = 0;
  
  time_now = millis();
  while (millis() < (time_now + captureWindow))
  {
    currentValue = analogRead(adcPin);
    if(currentValue > maxValue){
      maxValue = currentValue;
    }
  }
  return maxValue;
}

// Short, low intensity haptic pulse
void movePulse(void){
  analogWrite(hapticPin,125);
  delay(90);
  analogWrite(hapticPin,0);  
}

// Long, high intensity haptic pulse
void clickPulse(void){
  analogWrite(hapticPin,250);
  delay(300);
  analogWrite(hapticPin,0);
}

void setup(void){
  // Pin mode configuration
  pinMode(bitePin, INPUT);
  pinMode(fsrPins[0], INPUT);
  pinMode(fsrPins[1], INPUT);
  pinMode(fsrPins[2], INPUT);
  pinMode(fsrPins[3], INPUT);
  pinMode(hapticPin, OUTPUT);
  digitalWrite(hapticPin, LOW);

  Serial.begin(9600); 
  Keyboard.begin(); 
  delay(200); 
  
  // Read out the calibration data stored in flash memory
  cal = calibration_storage.read();

  // If this is the first run the "valid" value will be "false"...
  if(cal.valid == false){
    delay(1000); // Allow extra time for the host system to recognize the keyboard interface
    calibrate();
    // Sanity check the new calibration data
    cal.valid = check_calibration();
    calibration_storage.write(cal);

    // Only initiate mouse control if the calibration was successful
    if(cal.valid == true){
      Serial.print("Calibraton checks out");
      Keyboard.println("Calibration complete! Activating the BYTE now."); 
      Mouse.begin();
    }
    else{
      Serial.print("There was a problem with calibration!");
      Keyboard.println("Problem with Calibration! Check connections and retry.");
    }
  } 
}
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

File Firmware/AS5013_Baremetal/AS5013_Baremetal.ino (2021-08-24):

#include <Wire.h>    

#define ADDR 0x41 // 0x40 alternative address.

#define nRESET 14   // Microcontroller pin number for reset connection
#define INT 15      // Microcontroller pin number for interrupt connection


#define CTRL_REG_1 0x0F  // 8-bit configuration register. (def: 11110000)
//  bit 7     1 = active mode, 0 = low power mode
//             AS5013 MUST be in low power mode for INT on threshold mode!
//  bits 6:4  low power readout time base register. Wake-up interval for low
//             power mode output:
//             000 -> 20ms, 001 -> 40ms, 010 -> 80ms, 011 -> 100ms
//             100 -> 140ms, 101 -> 200ms, 110 -> 260ms, 111 -> 320ms
//  bit 3     1 = interrupt disabled, 0 = interrupt enabled
//  bit 2     0 = INT pin low on every new coordinate calculation
//            1 = INT pin low when threshold values exceeded and while
//                threshold values are exceeded
//  bit 1     write to 1 to reset device
//  bit 0     1 = conversion complete, data valid. Read only!


#define T_CTRL_REG_2 0x2E   //Register to configure the magnet polarity
                            // 0x84 meaning not swaped polarity (default)
                            // 0x86 meaning swaped polarity

#define T_CTRL_REG 0x2D    // Scaling factor for X/Y coordinates.
//  Datasheet says to set this to 0x06 which is NOT the default power-up value.

#define ID_CODE_REG 0x0C   // 8-bit manufacturer ID code. Read only.
//  Reads as 0x0C- useful to test data communications with the device.

#define X_REG 0x10         // 8-bit register containing a signed 8-bit
                                   //  X coordinate
                                   
#define Y_REG 0x11         // Y position register. Reading this register
                                   //  resets the status of the INT output, so it
                                   //  should be read AFTER the X value.
                           
// INT threshold registers. If the X or Y value is greater than the value in the
//  corresponding "P" register or less than the value in the "N" register, and 
//  JS_Control_Register_1 bit 2 = 1 and bit 3 = 0, and the device is set to poll
//  its read values automatically, 
#define XP_REG 0x12
#define XN_REG 0x13
#define YP_REG 0x14
#define YN_REG 0x15

char XZero = 0;
char YZero = 0;
int16_t sensorData=0;

void setup() 
{ 
  Serial.begin(9600);  
  Wire.begin();        
  pinMode(INT, INPUT_PULLUP);  
  pinMode(nRESET, OUTPUT); // The reset line to the EasyPoint should be output.
  
  AS5013_Init();  
  AS5013_Int_Setup(XZero, YZero, 25, 25); 

  Serial.println("Setup completed successfully.");
} 


void loop() 
{ 
  if(digitalRead(INT)==LOW)
  {
    Serial.println("INT!!!!");
    for(int i=1;i<6;i++){
       Serial.println("Sensor "+String(i)+" = "+String(AS5013_Read_Raw(i)));
    }
    Serial.println(readXAxis(), DEC); // readXAxis() returns a signed 8-bit result.
    Serial.println(readYAxis(), DEC); // readYAxis() returns a signed 8-bit result.
    
  }
}

// A simple function for setting the internal interrupt function to flag the
//  processor if the joystick moves more that x_delta or y_delta units from
//  the points specified by x_null and y_null. A function to set up an
//  asymmetrical dead zone is left as an exercise for the reader; the principle
//  is the same- write the appropriate registers, etc etc.
void AS5013_Int_Setup(char x_null, char y_null, byte x_delta, byte y_delta)
{
  char xp, xn, yp, yn;  // 8-bit signed values for the trigger points.
  xp = x_null + x_delta;  // calculate the positive trigger point for x
  writeI2CReg(ADDR, XP_REG, xp);  // set the positive trigger point for x
  xn = x_null - x_delta;  // calculate the negative trigger point for x
  writeI2CReg(ADDR, XN_REG, xn);  // set the negative trigger point for x
  yp = y_null + y_delta;  // calculate the positive trigger point for y
  writeI2CReg(ADDR, YP_REG, yp);  // set the positive trigger point for y
  yn = y_null - y_delta;  // calculate the negative trigger point for y
  writeI2CReg(ADDR, YN_REG, yn);  // set the negative trigger point for y
  

  byte temp = readI2CReg(ADDR, CTRL_REG_1);
  // clear bit 3, INT pin is active.
  temp = temp & 0b11110111;
  // Then, clear bit 7, self-timed mode (otherwise,
  //  it will only do a conversion after a read, which means you need to poll
  //  it to initiate a read, which makes the INT pin useless).
  temp = temp & 0b01111111;
  // Now, clear bits 6:4, so we can set the polling rate. See register description
  //  above for details on various values of these bits.
  temp = temp & 0b10001111;
  // Set the bits according to the desired polling rate. Here, 200ms.
  temp = temp | 0b01010000;
  // Then, set bit 2, to tell the device to interrupt based on range and not
  //  every time a conversion is complete.
  temp = temp | 0b00000100;

  // Finally, write the adjusted value back into Control Register 1.
  writeI2CReg(ADDR, CTRL_REG_1, temp);
}
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

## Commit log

2020-08-31 Initial Upload
    [BYTE_Control_Board.kicad_pcb, BYTE_Control_Board.sch, Byte_108.FCStd]
2020-09-10 Including printable part models
    [BYTE_108_Button.amf, BYTE_108_Retainer.amf, BYTE_108_Stem_Bottom.amf, BYTE_108_Stem_Middle.amf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]
2020-09-11 Including Enclosure Design
    [Controller_Enclosure_06.FCStd, Controller_Enclosure_06_Bottom.amf, Controller_Enclosure_06_Top.amf]
2020-09-11 Including Bill of Materials
2021-08-13 add hardware folder
    [BYTE_Control_Board.kicad_pcb, BYTE_Control_Board.sch]
2021-08-13 add mechanical folder
    [BYTE_108_Button.amf, BYTE_108_Retainer.amf, BYTE_108_Stem_Bottom.amf, BYTE_108_Stem_Middle.amf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]
2021-08-18 PCB Manufacturing Artwork
    These SVG files contain the geometry required for the sensor pack PCBs
2021-08-18 Sensor PBC artwork
    Re-arranging the folder structure
2021-08-23 Add sensor pack folder for different sensors KiCad projects
    [BYTE_Bite.kicad_pcb, BYTE_Bite.sch, BYTE_FSR.kicad_pcb, BYTE_FSR.sch]
2021-08-24 add magnetic sensor test firmware with arduino
2021-08-30 add projects
    [BYTE_Bite.kicad_pcb, BYTE_Bite.sch, BYTE_Capacitive.kicad_pcb, BYTE_Capacitive.sch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]
2021-09-06 update capacitive ICs
    [BYTE_Capacitive.kicad_pcb, BYTE_Capacitive.sch]
2021-09-06 add magnetic sensing
    [BYTE_Magnetic.kicad_pcb, BYTE_Magnetic.sch]
2021-09-06 update sch magnetic
    [BYTE_Magnetic.sch]
2021-09-08 update capacitive sensor board
    [BYTE_Capacitive.kicad_pcb, BYTE_Capacitive.sch, BYTE_Capacitive.step, BYTE_Magnetic.step]
2021-09-08 update magnetic layout
    [BYTE_Magnetic.kicad_pcb, BYTE_Magnetic.sch, BYTE_Magnetic.step]
2021-09-13 modify magnetic
    [BYTE_Capacitive.kicad_pcb, BYTE_Magnetic.kicad_pcb, BYTE_Magnetic.step]
2021-09-15 add footprint for FSR and LRA motor
2021-09-15 update magnetic sensor, merge with FSR
    [BYTE_Magnetic.kicad_pcb, BYTE_Magnetic.sch]
2021-09-15 add motor footprint
    [BYTE_Capacitive.kicad_pcb, BYTE_Capacitive.sch, BYTE_Capacitive.step]
2021-09-21 modify controller board
    [BYTE_Control_Board.kicad_pcb, BYTE_Control_Board.sch]
2021-09-22 update pcbs
    [BYTE_Capacitive.kicad_pcb, BYTE_Control_Board.kicad_pcb, BYTE_Control_Board.sch, BYTE_Magnetic.kicad_pcb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]
2021-09-22 update gnd route
    [BYTE_Magnetic.kicad_pcb]
2021-09-23 update magentic adding I2C I/O controller
    [BYTE_Magnetic.kicad_pcb, BYTE_Magnetic.sch]
2021-09-23 update controller PCB added battery reading circuit
    [BYTE_Control_Board.kicad_pcb, BYTE_Control_Board.sch]
2021-09-24 update magnetic sensor
    [BYTE_Magnetic.kicad_pcb, BYTE_Magnetic.sch]
2021-09-28 update magnetic pcb and
    [BYTE_Magnetic.kicad_pcb]
2021-09-30 update byte controller
    [BYTE_Control_Board.kicad_pcb, BYTE_Control_Board.sch]
2021-10-02 update controller to v1.1
    [BYTE_Control_Board.kicad_pcb]
2021-10-02 move ICs 0.5 to center, magnetic sensor
    [BYTE_Magnetic.kicad_pcb]
2021-10-04 update byte controller for hand made
    [BYTE_Control_Board.kicad_pcb]
2021-10-05 add byte panel for manufacture
    [BYTE_PANELkicad_pcb-B_Adhes.gbr, BYTE_PANELkicad_pcb-B_Cu.gbr, BYTE_PANELkicad_pcb-B_Mask.gbr, BYTE_PANELkicad_pcb-B_Paste.gbr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]
2021-10-07 prepare for manufacture
    [BYTE_Bite-B_Adhes.gbr, BYTE_Bite-B_Cu.gbr, BYTE_Bite-B_Mask.gbr, BYTE_Bite-B_Paste.gbr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]
2021-10-07 modify gerbers
    [BYTE_Bite_Base-B_Adhes.gbr, BYTE_Bite_Base-B_Cu.gbr, BYTE_Bite_Base-B_Mask.gbr, BYTE_Bite_Base-B_Paste.gbr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]
2021-10-11 add manufacturer part number for BOM
    [BYTE_Control_Board.sch, BYTE_Magnetic.sch]

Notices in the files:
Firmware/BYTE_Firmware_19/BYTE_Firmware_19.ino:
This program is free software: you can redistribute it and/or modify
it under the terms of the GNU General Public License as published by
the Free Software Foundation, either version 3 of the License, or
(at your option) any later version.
